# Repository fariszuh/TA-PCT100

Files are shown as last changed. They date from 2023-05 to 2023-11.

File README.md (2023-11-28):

# Tugas  Akhir PCT-100
Repository ini berisi file tugas akhir Implementasi PCT-100.
File yang tersedia berisi file program TA yang dibuat Penulis Muhammad Faris Zuhairi (2019 / Wisudawan 128 ITS), 
dengan judul berikut:

PERANCANGAN KONTROLER TERTANAM MENGGUNAKAN DIRECT NEURAL NETWORK UNTUK PENGATURAN LEVEL TANGKI PCT-100

Link Tugas Akhir: https://repository.its.ac.id/98936/ 
atau pada direktori "**Faris's Undergraduate Thesis (Buku TA)/07111940000164-Undergraduate_Thesis.pdf**"

Berikut foto prototype yang dibuat dan dihibahkan ke Lab. Kontrol dan Otomasi Dept. Teknik Elektro ITS

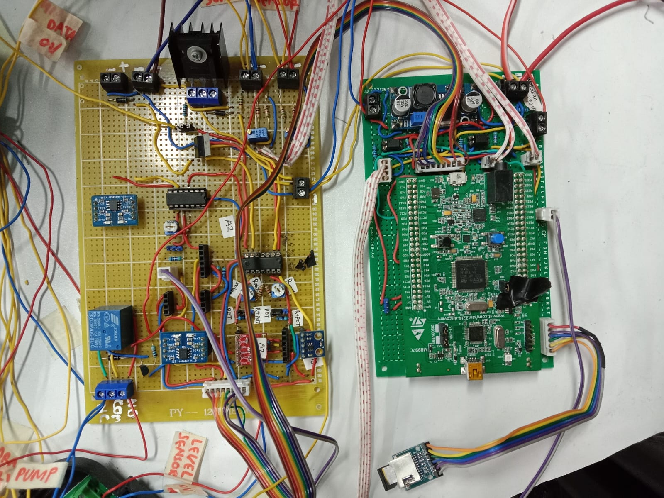
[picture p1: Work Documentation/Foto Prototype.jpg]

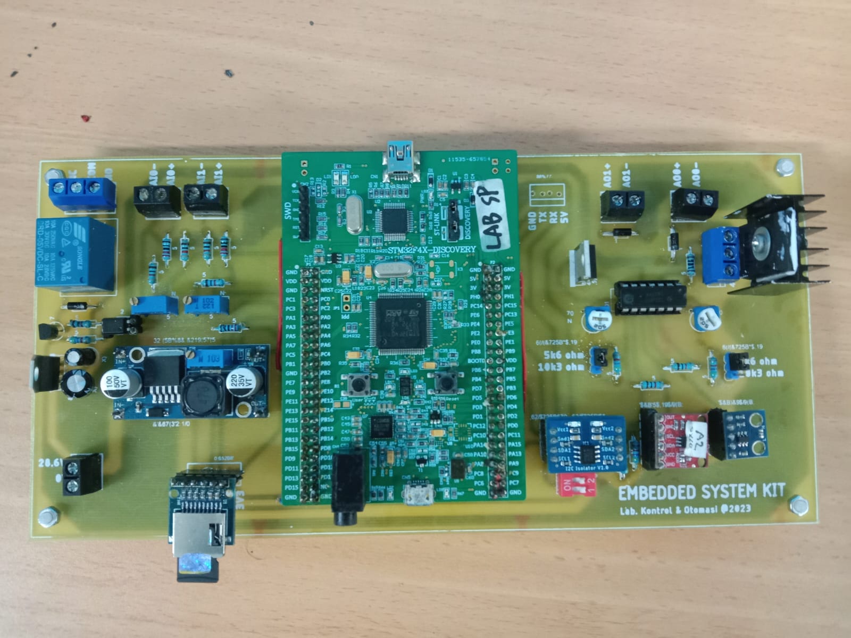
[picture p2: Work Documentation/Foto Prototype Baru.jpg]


## 1. Tahap Permodelan
Tahap ini model plant diambil menggunakan identifikasi plant dan penurunan rumus. 
Permodelan dimulai dengan mengambil data menggunakan STM32 dengan hasil datasets terdapat pada folder berikut:
+ **/Datasets for Modelling & Test Result/**
  - **/Karakteristik Drain Valve/** :
  Data yang digunakan untuk memodelkan drain valve.

    Divariasikan: tegangan drain (Vdrain) dan tegangan flow control valve (Vfc).
    Dijaga konstan: tegangan pompa (Vpompa) 10V.

  - **/Karakteristik Flow Control Valve/** :
  Data yang digunakan untuk memodelkan flow control valve.

    Divariasikan: tegangan pompa (Vpompa) dan tegangan flow control valve (Vfc).
    Dijaga konstan: tegangan drain (Vdrain) tertutup (0 VDC).

  - **/Karakteristik Pompa/** :
  Data yang digunakan untuk memodelkan pompa inlet.

    Divariasikan: tegangan pompa (Vpompa).
    Dijaga konstan: tegangan drain (Vdrain) tertutup (0 VDC) dan dan tegangan flow control valve (22 VDC).

  - **/Karakteristik AI USB4716/** :
    Hasil pengujian DAC Amplifier AO STM32 dengan AI USB4716.
    Pengambilan data ini tanpa menghubungkan prototype ke plant (actuator dan sensor).
    Kode pengujian ini ada di folder **/Pengujian (Testing)/**.
  
    Divariasikan: tegangan AO STM32.

  - **/Karakteristik AO USB4716/** :
    Hasil pengujian ADC AI STM32 dengan AO USB4716.
    Pengambilan data ini tanpa menghubungkan prototype ke plant (actuator dan sensor).
    Kode pengujian ini ada di folder **/Pengujian (Testing)/**.

    Divariasikan: tegangan AO USB4716.

  - **/Pengujian NN/Implementasi/** :
    Hasil pengujian algoritma NN yang ditanam pada STM32.
    Pengambilan data ini dengan menghubungkan prototype ke plant (actuator dan sensor).
  
    Divariasikan: learning rate konstan dan nilai alpha (adaptasi learning rate) --> sudah dipisahkan dalam 2 folder yang berbeda.

  - **/Rafif Firdiansyah's Level Sensor Data/** :
    Excel workbook pembacaan tegangan level sensor dan simpangannya dengan level aktual (cm).

  - **/With Both Drain Valve/** :
    Data yang digunakan untuk memodelkan kedua valve pada kondisi berikut:
    Terbuka: manual dan motor drain valve.
    Tertutup: tidak ada.

      Divariasi: tegangan drain (Vdrain).
    
      Dijaga konstan: tegangan pompa (10 Vpompa) dan tegangan flow control valve (15 Vfc).
  
  - **/with Manual Valve/** :
    Data yang digunakan untuk memodelkan manual valve pada kondisi berikut:
    Terbuka: manual drain valve.
    Tertutup: motor drain valve --> tegangan drain (0 Vdrain) .

      Divariasi: tegangan pompa (Vpompa), dan tegangan flow control valve (Vfc).
    
      Dijaga konstan: full open manual valve.

  - **/with Proportional Drain Valve/** :
    Data yang digunakan untuk memodelkan motor valve pada kondisi berikut:
    Terbuka: motor drain valve.
    Tertutup: manual drain valve.

      Divariasi: tegangan flow control valve (15 Vfc).
    
      Dijaga konstan: tegangan drain (Vdrain) dan tegangan pompa (Vpompa).

Sedangkan, folder berikut berisi file program DAQ untuk pengambilan data plant.

+ **/MATLAB USB-4716/** : pengambilan data melalui DAQ Advantech USB-4716
  - **/Code TA Dedy Motor Induksi & Altivar 610/** : 
  Kode dan Tugas Akhir Dedy / Bambang Permadi Widyasmara tentang Kontrol PID-GA Motor Induksi.
    - Call.m : file utama yang hanya di run untuk mulai mengambil dan mengirim data.
    - ReadWrite.m : file library yang dibuatkan Faris (tidak perlu diubah-ubah).
    
  - **/Code USB4716 TA Faris (Worked)/** :
  File yang sudah diuji dan berhasil membaca AI dan mengirim AO.
    - **/Hasil Pengujian ADC-DAC STM32 dengan USB4716/** :
    Berisi file .mat workspace MATLAB pembacaan pengujian sinyal ramp AI dan AO dari Kit STM32 Implementasi.
    - CascadeController.m : mencoba menyusun kontroler cascade berdasarkan AI-AO
    - InstantAI.m : library default MATLAB untuk analog input DAQ
    - NN.m : mencoba menyusun kontroler Direct NN
    - Static_AO.m : library default MATLAB untuk analog output DAQ
    - Static_AO_custom.m : perubahan Static_AO.m agar bisa mengirim sinyal berubah2 (tidak terbatas default sawtooth, sine, square, dll)
    - Static_AO_simple.m : simplifikasi dari Static_AO_custom.m
  - **/Library Example Bawaan Navigator App/** :
  Library MATLAB yang didapatkan dari tutorial aplikasi Navigator.exe.
  - **/Library python-advantech-DAQNavi-bdaqctrl/** : 
  Library python untuk USB-4716, masih perlu compiler dari C ke python

+ /regresi : regresi respon level dan flow untuk mendapat gain scaling transmitter
  - regresi_FT.m : mencari gain flow meter untuk mengubah tegangan volt ke debit liter/menit (lt/min)
  - regresi_LT.m : mencari gain level sensor untuk mengubah tegangan volt ke level (mm)
+ /write_csv : testing program python data logger
  - save_data_fopen.py : test buka data csv menggunakan fungsi fopen()
  - save_data_withopen.py : test buka data csv menggunakan fungsi withopen()

## 2. Tahap Simulasi
Model yang telah diperoleh pada tahap sebelumnya digunakan untuk desain kontroler. 

+ **/Modelling & PCT-100 Simulation Testing/** :
  - **/MAT simulasi/** : 
  Berisi file .mat workspace MATLAB. Setpoint/SP divariasikan 100mm dan dynamic naik turun.
  MOV divariasi bukaan mulai 0%, 50% (aka 0.5), 100% (aka 1), dan dynamic (uniform random).
  Untuk Learning Rate (lr) konstan, alpha=0 dan lrinit divariasi mulai dari 1e-5 hingga 5.
  Namun, untuk Adaptasi Learning Rate melalui parameter alpha, divariasikan alpha mulai 1e-4 hingga 0.1, dimana alpha identik dengan kecepatan perubahan learning rate (lr).
  
  - **/Proteus DAC PWM/** :
  Berisi simulasi proteus untuk rangkaian PWM generator, amplifier teganan AO, dan filter sebelum diimplementasikan bersama STM32.
  
  - **/Tank Level Modelling/** :
  Simulasi kontroler berdasarkan model. Namun file terbarunya berada diluar folder ini (upper directory sekali).
  - closedLoop.slx : Simulink closed loop system
  - loadDatasets.m : file function matlab untuk membuka datasets untuk permodelan/menampilkan grafik respon
  - modellingDatasets.m : pengolahan raw data plant untuk mendapatkan gain scaling model
  - openLoop.slx : Simulasi open loop system

+ **/Pengujian (Testing)/** : Berisi kode untuk pengujian performa kontroller.
  - pengujian_ADC_AI_STM.m : pengujian ADC AI STM32 dengan menginjeksi tegangan AO sinyal ramp naik turun pada USB4716.
  - pengujian_ADC_A0_STM.m : pengujian DAC A0 STM32 dengan DAC STM32 menginjeksi tegangan sinyal ramp naik turun ke USB4716.
  - pengujian_lr.m : berisi kode untuk plot hasil model NN satu satu dari datasets.

## 3. Tahap Implementasi

+ **/Datasheet and Manual Embedded System Kit/** :
  Berisi datasheet dan manual komponen prototype Embedded System Kit.
  - **/ADAM 5000L-TCP/** : 
  Folder berisi Advantech ADAM5000L TCP installer, modbus simulator, dan RD9700 USB-Ethernet Driver
  
  - **/Manual Advantech USB4716/** :
  Folder berisi datasheet Advantech USB4716 dan Tugas Akhir yang menggunakan perangkat DAQ ini.
  Installer DAQ ini dapat didownload terbaru pada laman resmi Advantech, aplikasi utility dan drivernya ialah Navigator.exe.

  - **/Manual PCT100 by Bytronic/** :
  Folder berisi datasheet PCT-100 dan Burkert Proportional Valve 2835D.

+ **/Embedded System Kit PCB & Acrylic Box/** :
Berisi file PCB dan 3D Akrilik.
  - **/3D Akrilik/** :
  Berisi file cetak akrilik dan gcode 3D print casing USB-TTL Converter. 
  - **/Schematic PCB/** :
  Berisi file PCB Eagle.

+ **/Faris's Undergraduate Thesis (Buku TA)/** :
Berisi dokumen Seminar Tugas Akhir (STA Himatektro ITS) dan Tugas Akhir Faris.

+ **/Konten Sidang (Thesis Defense) dan Proposal/** :
Berisi file proposal (dokumen dan PPT sidang sempro) dan PPT sidang TA.

+ **/Manual Book Embedded System Kit/** :
Berisi manual book dari prototype Embedded System Kit yang sudah dibuat.
Harap pengguna prototype dan asisten Lab. Kontrol dan Otomasi ITS mempelajari ini.

+ **/PCT100 with ADAM 5000L MQTT/** :
  Implementasi PCT100 untuk TA Khoiruz (PID-PSO) dan TA Rafif (fuzzy MQTT) menggunakan ADAM5000L/TCP.

  - **/Modelling & Testing/** : Pengujian kontroler fuzzy dan PID dituning PSO
    - **/Datasets/** : Hasil pengambilan data openloop untuk TA Khoiruz dan Rafif
    - **/multiple subscribe fuzzy/** : testing program MQTT subscribe untuk kontroler fuzzy
        * Close Loop Fuzzy Multiple Subscribe.py : subscribe untuk closed loop system
        * MQTTtestMultipleSubscribe.py : test data masuk MQTT
    - **/scaling_regresi_flow_meter/** : 
    mencari gain scaling flow, raw data dari software PCT100 (bukan DAQ) oleh Khoiruz untuk permodelan plant. 
    - closedLoop_fuzzy.py : kontroler closed loop fuzzy
    - closedLoop_fuzzy_azzam.py : kontroler close loop fuzzy dengan rule base TA Hamzah Nur Azzam Motor Induksi
    - closedLoop_level.py : kontroler PID close loop level khoiruz
    - closedLoop_level_buTri.py : kontroler PID khoiruz hasil revisi penguji Bu Trihastuti
    - openLoop_level_flow.py : open loop untuk mendapat respon level dan flow identifikasi
    - readStreamModbus.py : Reverse engineering informasi stream Modbus UDP dari DAQ ADAM4000L/TCP
    - systemIdentification.py : Identifikasi sistem orde 1 + time delay dan orde 2 sesuai jurnal Jacoubek_Pavel
    - testRampMotorDC_SPA.py : pengujian sinyal kontrol ramp motor DC untuk tugas sistem pengaturan adaptif
    - testTs.py : pengujian untuk memperkecil timesampling Ts Modbus UDP DAQ ADAM4000L
    - testUDPmasAdrian.py : ambil data informasi AI UDP
    - testUDPmodbus2.py : ambil data informasi AI UDP dengan algoritma lain
  - **/Python GUI/** : Test coba desain GUI Python Modbus TCP
  - **/Regresi Sensor/** : berisi regresi level transmitter (LT) dan flow meter (FT).
  - **/Serial STM32/Send Command.py** : berisi kode untuk send command SP, Kp, Ki, Kd ke mikrokontroller STM32 sebagai parameter kontroller.
  - **/List Pin IO ADAM.xlsx** : List pin Input Output ADAM5000L dan berisi address register Modbus TCP.

+ **/Rafif's MQTT Mobile App/** : Settingan MQTT Rafif untuk kontroler fuzzy.
  - **/Konfigurasi APP IoT MQTT Panel/** : Konfigurasi IoT MQTT Panel (Aplikasi PlayStore).
  - testMQTT.py : implementasi python dengan app IoT MQTT Panel (playstore)

+ **/Receipt & Buying Report/** : Kumpulan nota dan laporan keuangan pembuatan prototype Embedded System Kit.
  Budget Rp1juta dari Lab. via Pak Eka Iskandar.
  - Rekap Nota Embedded System Kit_Update 19 Nov 2023.xlsx : Laporan keuangan masuk keluar dan total.

+ **/References for Citation/** : Kumpulan buku dan jurnal penelitian.
  - **/Faris's Journal Reference/** : 
  Referensi jurnal faris untuk neural network dan plant mathematical modelling.
  - **/PID ANFIS Hakhi** : 
  Referensi jurnal Hakhi berkaitan dengan ANFIS.
  - **/Previous Thesis/** : 
  Tugas akhir sebelumnya yang membahas coupled tank, PCT single tank, quadruple tank, NN, dan TA lain yang berkaitan.
  - **/System Identification Journal/** :
  Jurnal referensi identifikasi model system.
  - **/Theory Book/** :
  Buku teori yang dapat digunakan untuk dasar teori bab 2.

+ **/STM32/MultichannelADC/** : Pengujian kontroler dengan program yang sudah tertanam

## Documentation
+ **/Work Documentation/** : 
  berisi dokumentasi pekerjaan dengan Sobat PCT 2023.
### Faris's NN Implementation Video (showed during Final Project Presentation/Sidang TA)
1. PCT100 with constant Set Point https://www.youtube.com/watch?v=iwgPA4LB7lY&ab_channel=MuhammadFarisZuhairi
2. PCT100 with Increasing-Decreasing Set Point (step 50mm) https://www.youtube.com/watch?v=AL7DxppEuDM&ab_channel=MuhammadFarisZuhairi

### Team's Documentation
1. [28/03/2023 - Part 1 Paparan Progress Bimbingan TA PCT-100 at 23:24:33] https://youtu.be/hUXw9mhMRqU
2. [28/03/2023 - Part 2 Paparan Progress Bimbingan TA PCT-100 at 23:34:30] https://youtube.com/shorts/yUkm82Lsc_I
3. [28/03/2023 - Part 3 Paparan Progress Bimbingan TA PCT-100 at 23:35:58] https://youtu.be/i6Gw3u0Zylg
4. [28/03/2023 - Part 4 Paparan Progress Bimbingan TA PCT-100 at 23:44:26] https://youtu.be/1I7eSQTP36s
5. [29/03/2023 - Part 5 Paparan Progress Bimbingan TA PCT-100 at 23:04:08] https://youtu.be/HnbYzEy3LrQ

### Disclaimer
Apabila terdapat kebingungan pada program/struktur repository, silahkan menghubungi author IDLINE: fariszuh

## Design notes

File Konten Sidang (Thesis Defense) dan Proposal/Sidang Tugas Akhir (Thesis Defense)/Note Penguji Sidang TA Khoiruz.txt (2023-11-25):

1. TF harus pake statespace model
2. cascade setidaknya variabel yg dikontrol flow dan level (MIMO) bukan SISO.
3. Tuning PID harus dibandingkan dgn conventional ziegler nichols, conventional narik garris. 
Kp ziegler didekatin dgn Kp PSO
4. Implementasi: aktuatornya 1, yaitu pompa. pompa hanya kontrol level. 
Mintanya p ari kontrol flow, pasti harus ada aktuator lain, agar tidak SISO, seperti Valve.
5. P&ID salah gambar -bu tri, gaadda electric signal ke pump.

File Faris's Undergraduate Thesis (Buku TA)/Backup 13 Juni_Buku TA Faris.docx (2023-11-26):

TUGAS AKHIR – EE184801

PERANCANGAN KONTROLLER TERTANAM MENGGUNAKAN DIRECT SELF TUNING NEURAL NETWORK UNTUK PENGATURAN LEVEL TANGKI PCT-100

MUHAMMAD FARIS ZUHAIRI

NRP 07111940000164

Dosen Pembimbing

Eka Iskandar, S.T., M.T.

NIP 198005282008121001

Dr. Trihastuti Agustinah, S.T., M.T.

NIP 196808121994032001

Program Studi Teknik Sistem Pengaturan

Departemen Teknik Elektro

Fakultas Teknologi Elektro dan Informatika Cerdas

Institut Teknologi Sepuluh Nopember

Surabaya

2023

TUGAS AKHIR – EE184801

PERANCANGAN KONTROLLER TERTANAM MENGGUNAKAN DIRECT SELF TUNING NEURAL NETWORK UNTUK PENGATURAN LEVEL TANGKI PCT-100

MUHAMMAD FARIS ZUHAIRI

NRP 07111940000164

Dosen Pembimbing

Eka Iskandar, S.T., M.T.

NIP 198005282008121001

Dr. Trihastuti Agustinah, S.T., M.T.

NIP 196808121994032001

Program Studi Teknik Sistem Pengaturan

Departemen Teknik Elektro

Fakultas Teknologi Elektro dan Informatika Cerdas

Institut Teknologi Sepuluh Nopember

Surabaya

2023

FINAL PROJECT – EE184801

EMBEDDED CONTROLLER DESIGN USING DIRECT SELF TUNING NEURAL NETWORK FOR LEVEL CONTROL IN PCT-100 TANK

MUHAMMAD FARIS ZUHAIRI

NRP 07111940000164

Advisor

Eka Iskandar, S.T., M.T.

NIP 198005282008121001

Dr. Trihastuti Agustinah, S.T., M.T.

NIP 196808121994032001

Study Program Control System Engineering

Department of Electrical Engineering

Faculty of Intelligent Electrical and Informatics Technology

Institut Teknologi Sepuluh Nopember

Surabaya

2023

# LEMBAR PENGESAHAN

PERANCANGAN KONTROLLER TERTANAM MENGGUNAKAN DIRECT SELF TUNING NEURAL NETWORK UNTUK PENGATURAN LEVEL TANGKI PCT-100

TUGAS AKHIR

Diajukan untuk memenuhi salah satu syarat

memperoleh gelar Sarjana Teknik pada

Program Studi S-1 Teknik Sistem Pengaturan

Departemen Teknik Elektro

Fakultas Teknologi Elektro dan Informatika Cerdas

Institut Teknologi Sepuluh Nopember

Oleh : MUHAMMAD FARIS ZUHAIRI

NRP. 07111940000164

Disetujui oleh Tim Penguji Tugas Akhir :

1. | Eka Iskandar, S.T., M.T. | Pembimbing
2. | Dr. Trihastuti Agustinah, S.T., M.T. | Ko-pembimbing
3. | Nama dan gelar penguji | Penguji
4. | Nama dan gelar penguji | Penguji
5. | Nama dan gelar penguji | Penguji

SURABAYA

Juni, 2023

# PERNYATAAN ORISINALITAS

Yang bertanda tangan di bawah ini:

Nama mahasiswa / NRP | : | Muhammad Faris Zuhairi
Program studi | : | Teknik Sistem Pengaturan
Dosen Pembimbing / NIP | : | Eka Iskandar, S.T., M.T. / 198005282008121001 Dr. Trihastuti Agustinah, S.T., M.T. / 196808121994032001

dengan ini menyatakan bahwa Tugas Akhir dengan judul “Perancangan Kontroller Tertanam Menggunakan Direct Self Tuning Neural Network untuk Pengaturan Level Tangki PCT-100” adalah hasil karya sendiri, bersifat orisinal, dan ditulis dengan mengikuti kaidah penulisan ilmiah.

Bilamana di kemudian hari ditemukan ketidaksesuaian dengan pernyataan ini, maka saya bersedia menerima sanksi sesuai dengan ketentuan yang berlaku di Institut Teknologi Sepuluh Nopember.

Surabaya, 10 Juni 2023

Mengetahui,
Dosen Pembimbing 1 | Dosen Pembimbing 2
Eka Iskandar, S.T., M.T. | Dr. Trihastuti Agustinah, S.T., M.T.
NIP. 198005282008121001 | NRP. 196808121994032001

Mahasiswa

Muhammad Faris Zuhairi

NRP. 07111940000164

# ABSTRAK

PERANCANGAN KONTROLLER TERTANAM MENGGUNAKAN DIRECT SELF TUNING NEURAL NETWORK UNTUK PENGATURAN LEVEL TANGKI PCT-100

Nama Mahasiswa / NRP | : | Muhammad Faris Zuhairi/07111940000164
Departemen | : | Teknik Elektro FTEIC - ITS
Dosen Pembimbing | : | Eka Iskandar, S.T., M.T. Dr. Trihastuti Agustinah, S.T., M.T.

Abstrak

Kata kunci: PCT-100, Neural Network, Self Tuning, Sistem Tertanam

# ABSTRACT

PERANCANGAN KONTROLLER TERTANAM MENGGUNAKAN DIRECT SELF TUNING NEURAL NETWORK UNTUK PENGATURAN LEVEL TANGKI PCT-100

Student Name / NRP | : | Muhammad Faris Zuhairi/07111940000164
Department | : | Teknik Elektro FTEIC - ITS
Advisor | : | Eka Iskandar, S.T., M.T. Dr. Trihastuti Agustinah, S.T., M.T.

Abstract

Keywords: PCT-100, Neural Network, Self Tuning, Embedded System.

# DAFTAR ISI

# DAFTAR GAMBAR

# DAFTAR TABEL

# DAFTAR SIMBOL

# BAB 1 PENDAHULUAN

## 1.1 Latar Belakang

Saat ini industri proses banyak menerapkan sistem otomasi pengaturan level fluida. Fluida dipompa dan ditampung dalam tangki khusus yang memerlukan pengendalian agar memenuhi batas level yang diperbolehkan. Umumnya level air dianalisis dengan mengestimasi model linear yang merepresentasikan sifat dinamis dari level terhadap titik setimbangnya. Apabila ketinggian cairan tidak dikendalikan maka rantai proses produksi akan terganggu. Jika ketinggian cairan melebihi ketinggian yang diinginkan maka akan terjadi overflow atau cairan akan meluap sehingga mengganggu atau dapat merusak alat-alat lain. Sebaliknya jika ketinggian cairan kurang dari ketinggian yang diinginkan maka proses tidak akan bekerja. Oleh karena itu ketinggian suatu cairan harus dikendalikan dalam suatu industri.

Umumnya dalam industri, fluida dialirkan menggunakan pompa, laju massa diatur dengan control valve, dan ketinggian fluida dalam tangki dibaca oleh level transmitter. Namun, pengaturan level tangki memiliki karakteristik time-varying dan non linier. Kontroller PID membutuhkan parameter berbeda-beda (tuning ulang) untuk menyesuaikan respon yang cepat. PCT-100 merupakan miniatur sistem proses industri yang terdapat fasilitas untuk melakukan pengaturan terhadap empat buah variable kontrol, yaitu flow, level, suhu, dan tekanan. Level pada plant PCT-100 yang dikendalikan oleh flow control valve seringkali mengalami perubahan parameter dalam kondisi-kondisi tertentu, seperti adanya beban drain air keluar. Untuk mengatasi perubahan ini, diperlukan metode yang dapat belajar (learning) terhadap perubahan. Selain itu, flow control valve memiliki karakteristik khusus yakni daya suplai yang dibutuhkan besar yang membutuhkan penguatan dan hardware terpisah untuk menjalankannya.

Salah satu metode learning yang menggunakan algoritma cerdas ialah neural network. Algoritma ini dapat mempelajari perubahan beban pada plant dan akan otomatis melakukan updating bobot selama plant beroperasi sehingga mudah memenuhi spesifikasi kontrol yang diinginkan. Dengan struktur direct, kontroller dapat langsung memberikan sinyal kontrol sesuai berdasar error setpoint variable sistem yang dikendalikan. Namun, pemilihan learning rate pada propagasi balik masih perlu dilakukan manual berdasar hasil eksperimen, sehingga jika kurang tepat memungkinkan terjadinya overshoot level. Skema self tuning dapat ditambahkan agar learning rate dapat beradaptasi sesuai error level. Pada tugas akhir ini akan dirancang controller tertanam menggunakan self tuning direct neural network plant PCT-100 yang meminimalkan error steady state dan mengurangi overshoot.

## 1.2 Rumusan Masalah

Kontroller PID pada dasarnya bersifat tetap selama parameter P, I, dan D tidak diubah. Ketika terjadi perubahan parameter plant yang diakibatkan oleh pembebanan, sinyal kontrol yang diberikan tidak sesuai dengan kondisi plant saat ini sehingga muncul pelonjakan atau penurunan nilai. Pada level tangki PCT-100, kondisi ini dapat diakibatkan oleh perubahan beban drain valve selama sistem berjalan sehingga parameter kontroller perlu dituning ulang terus menerus. Penggunaan neural network sebagai direct controller memiliki keunggulan dapat beradaptasi pada model nonlinear, namun pemilihan learning rate masih dilakukan manual dengan eksperimen. Selain itu, flow control valve sebagai actuator memiliki daya suplai tinggi (0-24V, 1A) dan tidak bisa dijalankan oleh modul data actuisition yang tersedia. Berdasarkan masalah nonlinearity, learning rate, dan aktuator tersebut, dibutuhkan kontroller tertanam dan menambahkan self tuning learning rate yang dapat melakukan pemilihan learning rate yang sesuai secara langsung (online tuning) agar steady state error dapat minimum.

## 1.3 Batasan Masalah

Ruang lingkup penelitian ini membahas mengenai pengaturan level pada tangki. Pengendalian level dilakukan oleh flow control valve dengan tegangan pompa konstan. Batasan lain yaitu mengabaikan efek temperature dan pressure dalam tangki proses.

## 1.4 Tujuan

Tujuan yang diharapkan dari penelitian ini ialah rancangan kontroller tertanam neural network mampu mengatasi masalah nonlinearity, adaptasi learning rate, dan penguatan sinyal actuator untuk mendapat error steady state dan overshoot yang minimum.

## 1.5 Manfaat

Manfaat yang dapat diperoleh melalui tugas akhir ini diantaranya memberikan pengembangan metode kontrol dari pengaturan level tangki nonlinear dan memberikan skema penguatan actuator yang tidak dapat dijalankan oleh data actuisition module biasa.

# BAB 1 TINJAUAN PUSTAKA

## 1.1 Hasil Penelitian Terdahulu

Penelitian terdahulu digunakan untuk mengetahui metode dan hasil penelitian yang sudah dilakukan. Penelitian terdahulu diperlukan sebagai landasan dan acuan peneliti terhadap perbandingan dan hubungan antar variable yang diuji.

Penelitian plant PCT-100 oleh Rachmad Dwi Raharjo (2014) dilakukan dengan metode PID gain scheduling terhadap level proses. Identifikasi sistem dilakukan dengan metode Harriot dan divalidasi menggunakan ISE/Integral Square Error. Hasil yang diperoleh yakni kontroller PID gain scheduling dapat mengendalikan respon dinamis dalam simulasi dengan rata-rata error waktu tunak 0.06% dan 0.12% pada implementasi. Namun, nilai gain PID masih dipengaruhi variable tertentu yang berubah kontinu atau dengan kata lain gain scheduling hanya cocok untuk variasi yang terprediksi.

Penelitian level proses kemudian disempurnakan oleh penelitian M. Zakki Ghufron (2016) yang menggunakan self-tuning PID dengan pendekatan adaptif. Kontroller adaptif dapat memperbaiki kelemahan metode gain scheduling, dimana dapat bekerja pada variasi tak terprediksi. Nilai gamma memengaruhi kecepatan adaptasi kontroller self tuning PID. Kriteria square time-square error/STSE unggul karena memberikan error terkecil 3.64% saat simulasi dan 0.093% bila diberikan pembebanan. Namun, implementasinya masih memerlukan waktu learning yang lama dan memerlukan otomatisasi penentuan nilai gamma.

Berdasarkan penelitian PCT-100 sebelumnya, diharapkan desain kontroller PID yang detuning menggunakan metode neural network dapat memberikan waktu yang cepat dalam proses learning.

Gambar x. Training neuron

Penelitian direct neural network oleh memberikan hasil yang efektif untuk mengatur posisi sudut alloy manipulator dengan maksimum error 0.83°. Bobot (weight) neural network diperbarui berdasarkan feedback sensor posisi. Karakteristik nonlinear hysteresis 1 DOF manipulator dapat dihilangkan dan posisi sudut mengikuti set point yang berbentuk gelombang sinus.

## 1.2 Dasar Teori

### 1.2.1 PCT-100

PCT-100 merupakan mini-plant industry yang didesain untuk pembajaran berbagai aplikasi industry. Produk bytronic ini menggabungkan beberapa proses menjadi unit tunggal sehingga memberikan fleksibilitas dan kemudahan operasi sistem proses. Air sebagai fluida dalam process rig dapat dikendalikan melalui control box dan PC software. Besaran ini meliputi temperature, level, pressure, dan flow. Eksperimen dengan metode kontrol bervariasi dapat dilakukan dengan mudah untuk mendapatkan respon variable process yang diinginkan.

#### 1.2.1.1 Process Rig

Process rig merupakan plant utama tempat proses berlangsung. Air distilasi yang ditampung dalam sump tank dipompa ke seluruh sistem pada flow sekitar 3.2 liter/menit. Air dapat dialirkan langsung menuju process tank atau dibelokkan menuju cooler. Flow meter mengukur flow rate air yang masuk process tank dan level sensor akan mengukur ketinggian permukaannya. Di dalam process tank, pressure dan temperature air dapat diukur. Air dalam tangki ini dapat dikeluarkan melalui manual atau proportional drain valve untuk mengakhiri satu siklus proses. Process rig juga dilengkapi dengan digital display untuk menunjukkan temperature, flow, pressure, dan level saat ini, serta indicator on/off dari cooler, heater, diverter, dan drain valve. PCT-100 tersusun atas beberapa elemen berikut.

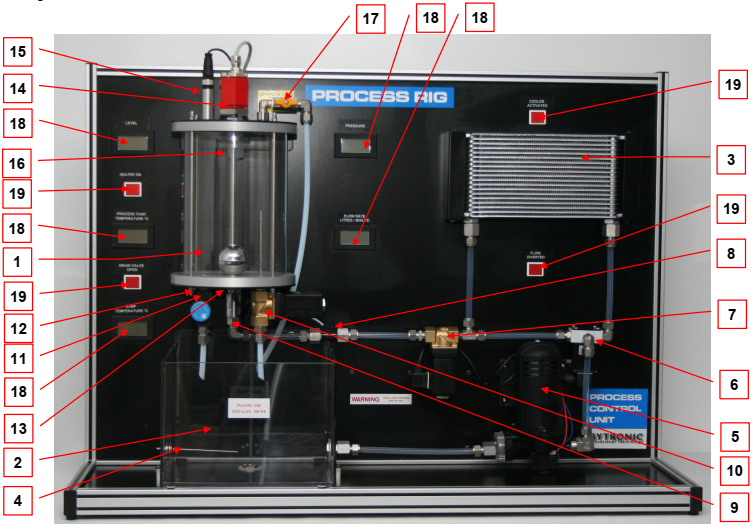
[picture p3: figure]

Gambar 2.1 Process Rig PCT-100

Tabel 2.1 Komponen process rig

No. | Perangkat
1 | Process tank
2 | Sump tank
3 | Cooler Unit
4 | Sump tank Temperature sensor (PRT)
5 | Variable speed pump with filter and pressure switch
6 | 3/2 Diverter valve
7 | 2/2 Proportional control valve
8 | Flow rate sensor
9 | One way check valve
10 | 2/2 Proportional drain valve
11 | Needle valve
12 | Pressure relief valve
13 | Heater
14 | Level sensor
15 | Pressure transducer
16 | Float switch
17 | Overflow/Vent valve
18 | Digital LCD displays
19 | Indicator lights

#### 1.2.1.2 Control Module

Control module merupakan perangkat yang berfungsi memberikan mengolah sinyal kontrol untuk diteruskan pada process rig. Control module mengolah sinyal input standar 0-10VDC menjadi tegangan suplai tiap actuator, serta mengkondisikan sinyal sensor menjadi sinyal standar 0-10VDC. Bagian depan perangkat ini menampilkan P&ID process rig yang dilengkapi dengan indicator on/off, fault switch, dan test point.

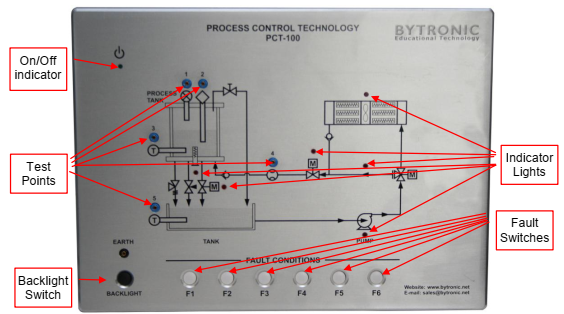
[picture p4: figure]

Gambar 2.2 Control Module

#### 1.2.1.3 Embedded Data Actuisition

Akuisisi data dilakukan untuk mengolah sinyal sensor sekaligus mengirimkan sinyal actuator dari dan ke control module. STM32F407VG digunakan sebagai mikrokontroller untuk memproses sinyal input 0-5V dan output ke DAC. MCP4725 DAC

### 1.2.2 Permodelan Plant

Sebelum melakukan desain kontroller, model plant perlu diketahui agar parameter kontroller sesuai dengan batas spesifikasi plant yang diimplementasi. Berikut merupakan arsitektur hardware PCT-100 beserta plant proses yang digunakan.

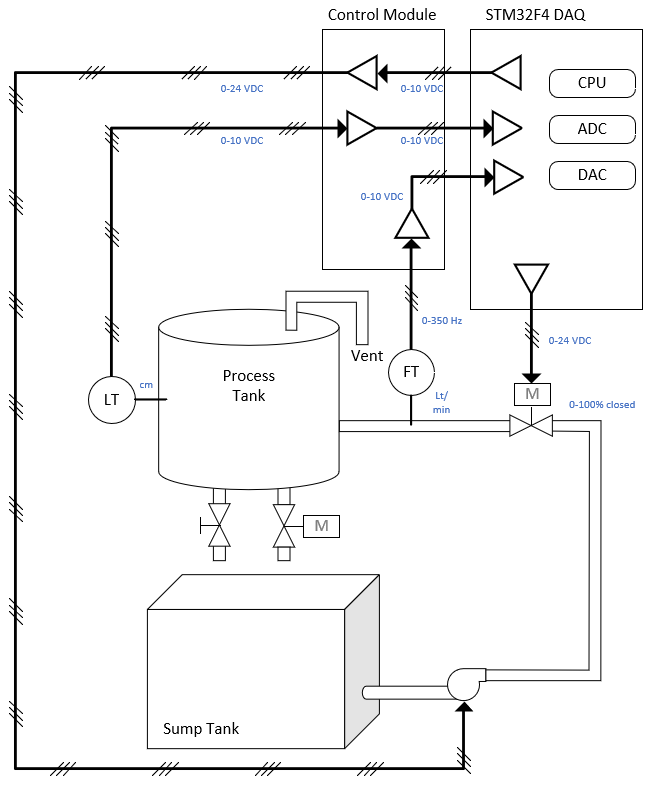
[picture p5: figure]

Gambar 2.2 Arsitektur Hardware PCT-100

#### 1.2.2.1 Permodelan Level Sensor

Level transmitter merupakan instrument pengukur ketinggian permukaan air menjadi tegangan searah dengan menggunakan level sensor. Pada level sensor terjadi konversi besaran ketinggian air menjadi tegangan. Faktor pengali ketinggian air ke tegangan dicari mula-mula dengan mengambil 4 sampel tegangan level sensor dari input ketinggian tertentu menggunakan jangka sorong, yakni 80.8mm, 128.4mm, 171.5mm, dan 208.15mm. Ketinggian air ini diambil pada jangkauan pergerakan floating ball untuk menghasilkan output tegangan sensor, yakni antara 30mm (bola mulai bergerak) hingga 210mm (bola berhenti bergerak). Secara konstruksi level sensor memiliki batas bawah awal bergerak dan batas akhir bergerak yang tergambar pada gambar dibawah.

Gambar 4.1 Penempatan floating ball pada tangki proses

Keluaran tegangan level sensor ( V_(LT) ) terhadap variasi ketinggian air (h), kemudian dilakukan regresi linier untuk mendapat persamaan garis lurus.

V_(LT) (h)=G_(LT) h+c_(LT)

G_(LT) =(V_(LT 4) -V_(LT 1))/(h_4 -h_1)

c_(LT) =V_(LT 4) -G_(LT) h_4

#### 1.2.2.2 Permodelan Flow Meter

Flow meter mengukur laju air masuk ke tangki proses. Laju ini dikenal dengan debit, yaitu laju volume per satuan waktu.

Q_(in) =(∆V)/(∆t)=A_(tabung) (∆h)/(∆t)

Input berupa laju air dikonversi oleh impeller turbin menjadi sinyal pulsa kemudian diproses signal conditioning. Output sensor flow ini ialah tegangan 0-10V. m_(FT) ialah factor konversi mikrokontroller dari input tegangan flow meter menjadi debit masukan.

Q_(in) =m_(FT) V_(FT)

Namun, model plant flow meter didapatkan dari input fisik laju ketinggian air (∆h)/(∆t) dan tegangan flow meter V_(FT) sebagai output sensor.

m_(FT) V_(FT) =A_(tabung) (∆h)/(∆t)

V_(FT) (h)=(A_(tabung))/(m_(FT))(∆h)/(∆t)

Misalkan gain model flowmeter adalah G_(FT) =(A_(tabung))/(m_(FT)) , model instrument flowmeter menjadi

V_(FT) (h)=G_(FT) (∆h)/(∆t)

#### 1.2.2.3 Permodelan Flow Control Valve

Permodelan flow valve ditujukan untuk mengetahui karakteristik bukan valve terhadap flow output pompa. Model flow control valve merupakan transfer function dari tegangan valve sebagai input dan flow rate air sebagai outputya. Model ini diperoleh dengan melakukan variasi tegangan valve, yakni 13V,15V,18V, dan 21V yang diperoleh terhadap tegangan step pompa 10V. permodelan flow control valve menggunakan metode vitechkova yang mengambil respon step saat 33% dan 70% nilai steady state. Sistem didekati oleh model orde 1 dengan menyertakan time delay model.

G_(V1) (s)=K/(τ_(V1) s+1)e^(-T_(dV1) s)

Dimana t_33 dan t_70 masing-masing ialah waktu 33% dan 70% dari nilai steady steate.

T_(dV1) =1.498t_33 -0.498t_70

τ_(V2) =0.794(t_70 -t_33 )

#### 1.2.2.4 Permodelan Drain Valve

Gambar 2.3 Bagan sistem tangki tunggal

Drain valve mengikuti prinsip konservasi energi, dimana persamaan Bernoulli menyatakan hubungan tekanan, laju fluida, dan ketinggian cairan dalam suatu tangki. Titik pada permukaan air dan dasar tangki bagian luar memiliki tekanan yang sama ( P_(permukaan) =P_(out) =1 atm ), namun memiliki kecepatan turun dan tinggi fluida yang berbeda.

P_(permukaan) +1/2ρv_(permukaan)^2 +ρgh_(permukaan) =P_(out) +1/2ρv_(out)^2 +ρgh_(out) =constant

1/2ρ(v_(out)^2 -v_(permukaan)^2 )=ρg(h_(permukaan) -h_(out) )

Kecepatan penurunan permukaan air dianggap sangat kecil sehingga diabaikan v_(permukaan) =0 dan lubang drain berada di dasar tangki h_(out) =0 .

1/2ρv_(out)^2 =ρgh

v_(out) =√(2gh)

Flow dapat dirumuskan sebagai laju air per satuan waktu, dengan A_O ialah luasan aperture drain valve.

Q_(out) =A_O v_(out) =A_O √(2gh)

#### 1.2.2.5 Permodelan Tangki

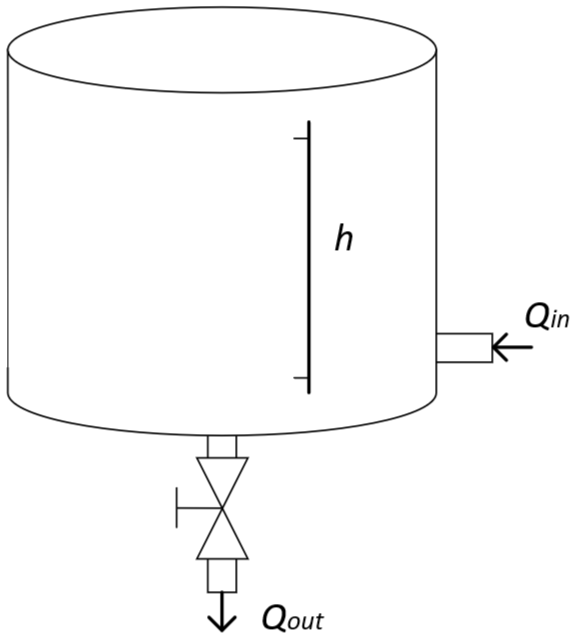
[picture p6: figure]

Gambar 2.5 Sistem tangki tunggal

Model dari tangki tunggal tampak pada gambar di atas. Untuk tangki ini, persamaan differensial level dapat dirumuskan sebagai berikut.

A_(tabung) h(t)=Q_(in) (t)-Q_(out) (t)

Dimana A_(tabung) : luas alas tabung, Q_(in) : flow air masuk tangki, Q_(out) : flow keluar tangki

A_(tabung) h(t)=Q_(in) (t)-A_O √(2gh)

Model ini menunjukkan dengan jelas persamaan nonlinear karena flow yang keluar tangki bergantung akar dari level tangki saat ini. Namun, persamaan tersebut dapat dilinearisasi dengan menganggap √h=h/√h seperti Berikut.

h(t)=bQ_(in) (t)-a(t)h(t)

Dimana b=1/(A_(tabung)) dan a(t)=(A_O √(2g))/(A_(tabung) √h)

Ketika h(t)=1 , parameter a(t) bernilai (A_O √(2g))/(A_(tabung) √h) sebagai lokasi pole ketinggian air. Lokasi pole ini terus mendapat scaling sejalan dengan akar dari level h saat ini. Transfer function sistem level orde 1 dapat dirumuskan melalui operator time derivative ‘s’ sebagai Berikut.

s h(t)=bQ_(in) (t)-a(t)h(t)

(s+a(t)) h(t)=bQ_(in) (t)

(h(t))/(Q_(in) (t))=b/(s+a(t))

a(t) dipilih pada posisi h tertentu saat valve drain full open dan memenuhi persamaan Berikut.

Q_(in) -Q_(out) =Ah

Q_(in) (t)-A_O √(2gh(t))=Ah

A_O √(2gh(t))=Q_(in) (t)-Ah

A_O =(Q_(in) (t)-Ah)/(√(2gh(t)))

Dimana h diambil dari gradien kurva level terhadap waktu, Q_(in) (t) dan h(t) masing-masing merupakan flow dan level air pada saat t tertentu.

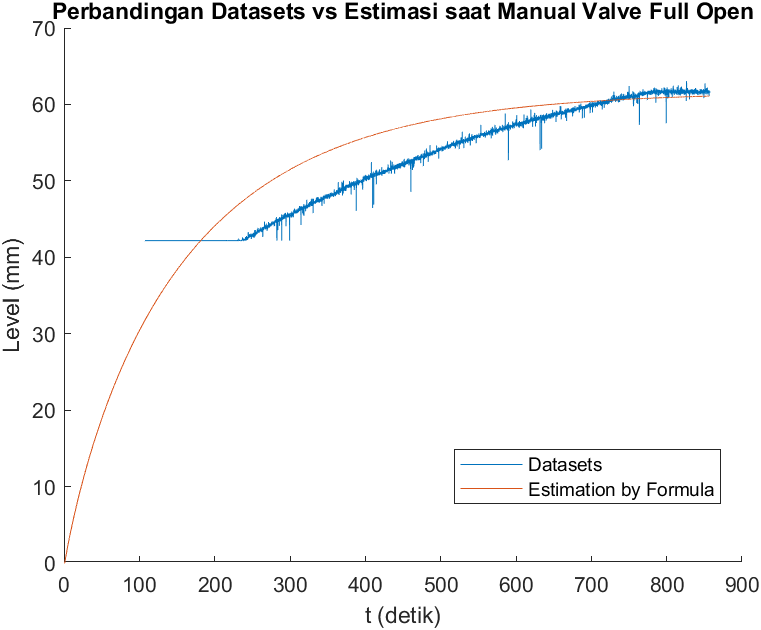
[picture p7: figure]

Gambar 3.2 Perbandingan datasets dengan estimasi model jika hanya manual valve full open

### 1.2.3 Direct Control Neural Network

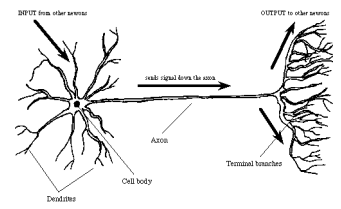
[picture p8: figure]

Gambar xx. Sel syaraf dan bagiannya

Neural Network bekerja menurut prinsip jaringan syaraf manusia. Dari Gambar di atas dapat dilihat, bahwa sebuah neuron mendapatkan input dari dendrit dan memberikan output melalui akson. Informasi masuk kedalam syaraf melalui dendrit. Dendrit ini bertugas mengumpulkan informasi dan meneruskannya ke badan sel. Pada badan sel, informasi yang telah dikumpulkan diolah dengan proses tertentu dan menghasilkan sinyal output. Output dari badan sel diteruskan ke sel syaraf berikutnya melalui akson. Akson ini akan terhubung dengan dendrit sel syaraf berikutya. Sambungan akson sel syaraf satu dengan dendrit sel syaraf lainnya disebut sinapsis. Kekuatan sambungan pada sinapsis menentukan seberapa besar informasi yang diteruskan oleh sel syaraf sebelumnya dapat diterima oleh sel syaraf berikutnya, yang kemudian disebut dengan bobot.

Tiruan neuron dalam struktur Neural Network adalah sebagai elemen proses yang dapat berfungsi seperti halnya sebuah neuron. Model dari neuron pada Neural Network ini seperti pada Gambar 2.8, dimana pi merupakan input pada neuron dan wi merupakan bobot atau weight. Sinyal input pi ini akan dikalikan dengan nilai wi. Nilai output dari neuron ini dapat dirumuskan seperti pada Persamaan berikut

Gambar xx. Blok diagram self-tuning neural regulator

Direct control neural network mengacu paga

Koefisien bobot w_(ji) dan v_j untuk hidden layer.

Untuk menurunkan algoritma backpropagation, cost function error dapat didefinisikan sebagai Berikut.

E(t)=1/2∑_(k=1)^t [e_y (k)]^2

S_j =∑_(i=1)^3 w_(ji) x_i

h_j =1/(1+e^(-S_j)), j=1,2,3…

r=∑_(j=1)^3 v_j h_j

u(t)=1/(1+e^(-r))

(∂E(t))/(∂v_j)=(∂E(t))/(∂e_y)(∂e_y)/(∂e_u)(∂e_u)/(∂u(t))(∂u(t))/(∂r)(∂r)/(∂v_j)

Dimana

(∂E(t))/(∂e_y)=(∂{1/2∑_(k=1)^t [e_y (t)]^2 })/(∂e_y)=e_y

(∂e_u)/(∂u(t))=(∂(u_d (t)-u(t)))/(∂u(t))=-1

(∂r)/(∂v_j)=(∂{∑_(j=1)^3 v_j h_j })/(∂v_j)=h_j

Turunan u(t) terhadap r(t)

(∂u(t))/(∂r)=(∂(1/(1+e^(-r))))/(∂r)=(e^(-r))/((1+e^(-r) )^2)

(∂u(t))/(∂r)=(e^(-r))/(1+e^(-r))1/(1+e^(-r))=u(t)[1-u(t)]

Dimisalkan δ^1 =e_y u(t) [1-u(t)]

(∂E(t))/(∂w_(ji))=-δ^1 v_j h_j (1-h_j )x_i (∂e_y)/(∂e_u)

Dimisalkan δ_j^2 =δ^1 v_j h_j (1-h_j )

(∂E(t))/(∂w_(ji))=-δ_j^2 x_i (∂e_y)/(∂e_u)

v_j (t+1)=v_j (t)+η sign((∂e_y)/(∂e_u)) δ^1 h_j

w_(ji) (t+1)=w_(ji) (t)+η sign((∂e_y)/(∂e_u)) δ_j^2 x_i

# BAB 2 METODOLOGI

## 2.1 Metode yang digunakan

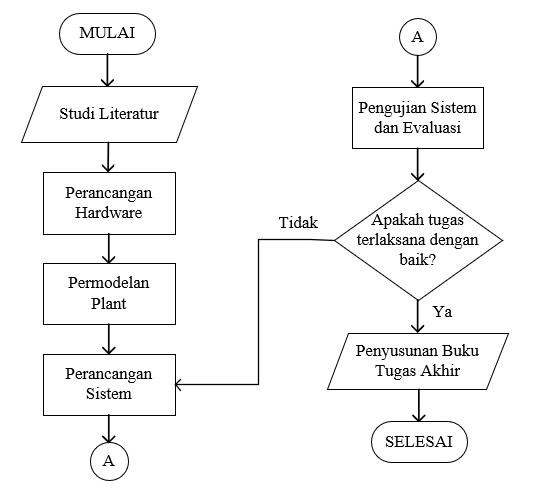
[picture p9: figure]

Gambar 3.3. Flowchart Metodologi Penelitian

Tahapan penelitian yang dilakukan pada tugas akhir ini tersaji pada flow chart gambar xx. Berikut penjelasan dari tahapan yang dilakukan tersebut.

1. Studi literatur

Tahap studi literatur digunakan untuk mengkaji teori-teori yang berhubungan perancangan kontroller sistem level dan desain rangkaian. Selain itu, dikaji pula konsep neural network dan proses learning. Sumber-sumber yang digunakan pada tahap ini berasal dari textbook, manual, datasheet, dan jurnal penelitian sebelumnya.

2. Perancangan hardware

Pada tahap perancangan hardware, hasil kajian tentang rangkaian digunakan sebagai bahan desain hardware. Perancangan ini meliputi desain mikrokontroller dan desain penggerak actuator. Hasil rancangan diuji dengan memberikan sampel sinyal dan mengevaluasi keluarannya apakah masih dalam range simpangan yang diperbolehkan.

3. Permodelan plant dan kontroller

Untuk mengidentifikasi model plant, rancangan hardware dijalankan untuk mendapatkan respon open loop sistem. Permodelan plant meliputi permodelan sensor, actuator, dan tangki proses. Metode identifikasi yang digunakan yaitu penurunan rumus fisis dan vitechkova. Setelah model plant dikatahui, didesain juga sistem closed loop dengan kontroller direct control neural network.

4. Pengujian sistem dan evaluasi

Pengujian sistem dilakukan melalui 2 tahapan, yaitu pengujian dengan simulasi dan pengujian implementasi. Rancangan kontroller disimulasikan pada software Simulink dan respon uji closed loop dievaluasi. Performa sistem berupa Agar algoritma simulasi dapat diimplementasi ke mikrokontroller, program Simulink perlu diubah menjadi Bahasa C. program ini kemudian ditanam pada mikrokontroller untuk pengujian implementasi. Respon implementasi menentukan keberhasilan model dan kontroller yang sudah didesain.

5. Penyusunan buku tugas akhir

Hasil penelitian yang sudah diperoleh kemudian disusun menjadi laporan berupa buku tugas akhir.

## 2.2 Bahan dan peralatan yang digunakan

Alat dan bahan yang digunakan dalam pengerjaan tugas akhir ini diantaranya ialah:

1. Plant PCT-100 sebagai plant utama yang ingin dikontrol
2. Laptop untuk simulasi dan penyusunan buku tugas akhir
3. STM32F407VGT6 Discovery sebagai mikrokontroller tempat program ditanam
4. Modul DAC MCP4725 untuk mengubah sinyal digital menjadi sinyal kontrol analog
5. Rangkaian voltage amplifier (LM324N dan Power MOSFET) sebagai modul penguatan sinyal kontrol ke actuator.

## 2.3 Urutan pelaksanaan penelitian

### 2.3.1 Permodelan Plant

#### 2.3.1.1 Permodelan Level Sensor

Respon tegangan sensor terhadap 4 sampel ketinggian air tampak pada gambar di bawah.

Gambar 4.1 Respon tegangan level sensor terhadap ketinggian air

Perhitungan gradien dan konstanta persamaan garis V_(LT) (h) digunakan 2 sampel level terendah h_0 =80.8mm dan tertinggi h_4 =208.15mm . Nilai tegangan pada kedua titik ini disubstitusi ke persamaan m dan c untuk memperoleh persamaan garis. G_(LT) merupakan gain level sensor dengan input berupa level dan output tegangan sensor.

G_(LT) =(9.4739-2.2046)/(208.15-80.8)=0.0571 Volt/mm

c_(LT) =9.4739-(0.0571*208.15)=-2.4076 Volt

Fungsi tegangan output V_(LT) (Volt) terhadap input ketinggian air level sensor h(mm) diperoleh sebagai fungsi persamaan linier berikut.

V_(LT) (h)=0.0571 h-2.4076

Fungsi level sensor untuk jangkauan dari dasar hingga dinding atas tangki dirumuskan oleh persamaan Berikut.

V_(LT) (h)={, 0 ;h<42.178mm, 0.0571 h-2.4076 ;42.178mm≤h≤217.324mm, 9.997 ;217.324mm≤h

h(V_(LT) )=(V_(LT) +2.4076)/0.0571=17.5189 V_(LT) +42.1780

#### 2.3.1.2 Permodelan Flow Meter

Identifikasi model flow meter diberikan dengan memberi variasi tegangan pompa. Berikut respon flow masuk tangki terhadap tegangan output pembacaan sensor V_(FT) .

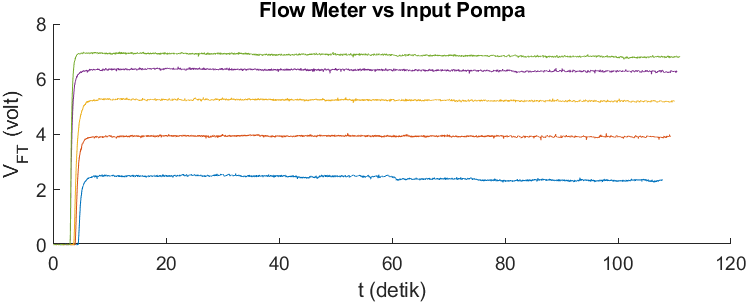
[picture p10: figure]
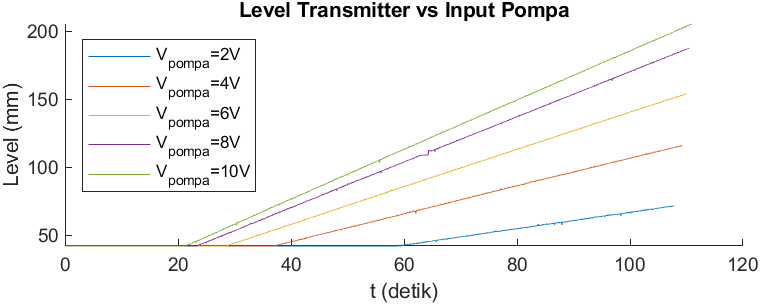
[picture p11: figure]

Gambar xx. Respon tegangan flow dan level terhadap variasi tegangan pompa

Perhitungan gain flow meter diperoleh dari pertambahan ketinggian air dan nilai steady state tegangan flow meter. Persamaan V_(FT) (h) merupakan persamaan garis lurus, sehingga gradien dan konstantanya dapat dicari berdasarkan sampel variasi flow. Variasi flow didapat dengan mengatur tegangan supply pompa, yakni 2V, 4V, 6V, 8V, dan 10V. Masing-masing tegangan ini terbaca flow meter sebesar 2.4011V, 3.9197V, 5.2441V, 6.3062V, dan 6.8518V.

V_(pompa) | V_(FT) steady state | Awal floating ball bergerak | | Setelah 120s runtime
| | t | V_(LT) | t | V_(LT)
2V | 2.4011 | 58837ms | 0 | 107873ms | 1.6992
4V | 3.9197 | 36762ms | 0.0171 | 109283ms | 4.2017
6V | 5.2441 | 28463ms | 0.0146 | 109974ms | 6.3794
8V | 6.3062 | 23408ms | 0.0098 | 110449ms | 8.3081
10V | 6.8518 | 21199ms | 0.0049 | 110928ms | 9.3140

Nilai V_(LT) ini kemudian dikonversi menjadi h dalam satuan mm oleh persamaan sebelumnya, yakni

h(V_(LT) )=17.5189 V_(LT) +42.178

Flow inlet tangki proses akan meningkatkan ketinggian air secara bertahap. Model flow meter didapatkan dalam kondisi drain valve tertutup dan floating ball berada pada jangkauan geraknya. Pada permodelannya, dihitung laju perubahan level naik ( dh/dt ) untuk mendapat tegangan flow meter V_(FT) sebagai output. Substitusi persamaan sebelumnya, V_(FT) (h)=(A_(tabung))/(m_(FT))(∆h)/(∆t) . A_(tabung) dan m_(FT) selalu tetap, namun V_(FT) berubah bergantung laju (∆h)/(∆t) sehingga dapat dirumuskan sebagai persamaan garis lurus V_(FT) (h)=(A_(tabung))/(m_(FT)) ((∆h)/(∆t))+c_(FT) seperti berikut.

gradien=(A_(tabung))/(m_(FT))=(V_(FT V_(pompa) =10V) -V_(FT V_(pompa) =2V))/(((∆h)/(∆t))_(V_(pompa) =10V) -((∆h)/(∆t))_(V_(pompa) =2V))

konstanta=c_(FT) =V_(FT t=120s) -((A_(tabung))/(m_(FT)))((∆h)/(∆t))_(t=120s)

Berdasarkan tabel diatas, substitusi untuk tiap variasi pompa diperoleh

V_(pompa) | V_(FT) (volt) | (∆h)/(∆t)(mm/ms)
2V | 2.4011 | 6.0358×10^(-4)
4V | 3.9197 | 0.001
6V | 5.2441 | 0.0014
8V | 6.3062 | 0.0017
10V | 6.8518 | 0.0018

Gambar 3.3 Respon tegangan flow meter V_(FT) terhadap laju level tangki ( ∆h/∆t ).

Dengan menggunakan rumus diatas diperoleh persamaan garis untuk flow:

(A_(tabung))/(m_(FT))=(6.8518-2.4011)/(0.0018-6.0358×10^(-4))=3666(Volt)/(mm/ms)

c_(FT) =6.8518-(3666)(0.0018)=0.253 volt

Substitusikan ke persamaan V_(FT) (dh/dt) :

V_(FT) ((dh)/(dt))=3666×(dh)/(dt)+0.253

Konstanta c_(FT) ini dapat diabaikan karena nilainya terlampau kecil dibandingkan range V_(FT) .

Diketahui A_(tabung) =πr_(tabung)^2 =8100π mm^2

(A_(tabung))/(m_(FT))=G_(FT) =3666

m_(FT) =(A_(tabung))/3666=(8100π)/3666=6.9408(mm^3)/(Volt. ms)

Maka diperoleh model flow meter untuk mengkonversi flow rate (lt/min) ke tegangan output V_(FT) di dalam mikrokontroller sebagai

Q_(in) =m_(FT) V_(FT) dalam (mm^3)/(ms)

Q_(in) =m_(FT) V_(FT) (6×10^(-2) ) dalam lt/min

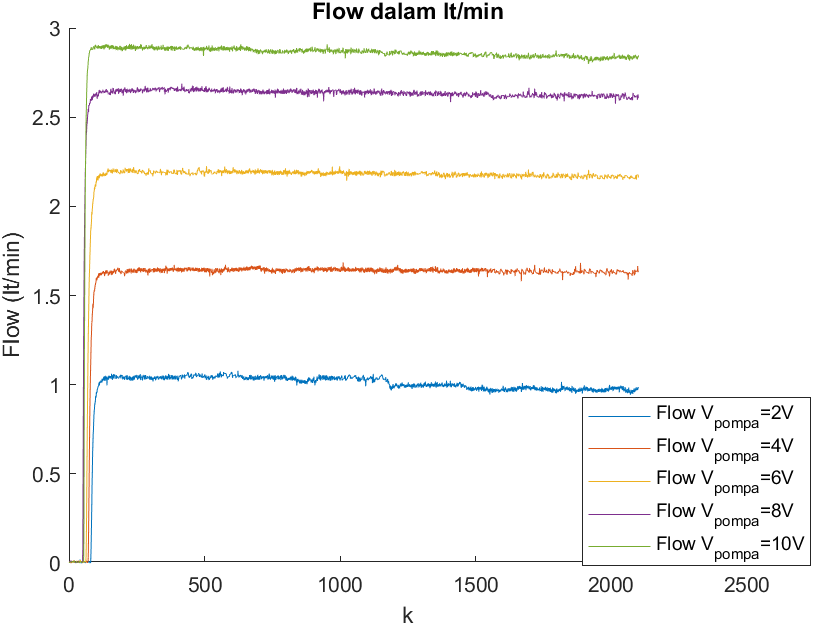
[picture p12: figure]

Gambar 4.4 Respon pembacaan flow meter terhadap variasi tegangan pompa setelah substitusi nilai gain m_(FT)

Model instrumen flow meter dengan input besaran fisis Q_(in) dan output V_(FT) diperoleh sesuai rumusan Berikut.

V_(FT) (h)=(A_(tabung))/(m_(FT))(∆h)/(∆t)

Misalkan model flowmeter adalah G_(FT) =(A_(tabung))/(m_(FT)) , model instrument flowmeter menjadi

V_(FT) (h)=G_(FT) (∆h)/(∆t)

Dimana G_(FT) =(A_(tabung))/(m_(FT))=3666(Volt)/(mm/ms)

#### 2.3.1.3 Permodelan Flow Control Valve

Berdasarkan variasi tegangan valve pada pengambilan data yang telah dilakukan, diperoleh waktu dan flow saat 33% dan 70% steady state yang tersaji dalam tabel Berikut.

Tabel 3.1. Parameter vitechkova tiap variasi tegangan valve ( V_(FC) )

No. | Vfc | y_(ss) | y_33 | t_33 | y_70 | t_70
1 | 13V | 1.7899 | 0.5907 | 0.0025 | 1.2529 | 0.0052
3 | 15V | 2.5560 | 0.8435 | 0.0023 | 1.7892 | 0.0043
4 | 18V | 2.9134 | 0.9614 | 0.0025 | 2.0394 | 0.0052
5 | 21V | 3.0639 | 1.0111 | 0.0014 | 2.1447 | 0.0022

Nilai t_33 dan t_70 digunakan untuk menghitung T_(dV1) dan τ_(V2) sesuai persamaan xx kemudian diperoleh MSE terbaik.

Tabel 3.2. Model vitechkova tiap variasi tegangan valve ( V_(FC) )

No. | Vfc | Kv1 | T_(dv1) | τ_(V1) | G(s) | MSE
1 | 13V | 0.1377 | 0.0012 | 0.0033 | 0.1377/(0.0033s+1)e^(-0.0012s) | 0.3849
3 | 15V | 0.1704 | 0.0013 | 0.0025 | 0.1704/(0.0025s+1)e^(-0.0013s) | 1.2362
4 | 18V | 0.1619 | 0.0011 | 0.0034 | 0.1619/(0.0034s+1)e^(-0.0011s) | 0.8319
5 | 21V | 0.1459 | 9.6676e-04 | 0.001 | 0.1459/(0.001s+1)e^(-0.000967s) | 8.1376

Model terbaik dipilih dengan syarat memiliki MSE kecil dan tidak terpengaruh pressure switch. Model Vfc=13V memiliki MSE kecil namun terpengaruh pressure switch (batas tegangan valve mulai terbuka, pressure switch pompa masih aktif). Model Vfc=18V dipilih selain MSE nya kecil, juga tidak terpengaruh pressure switch.

G_(valve) =0.1619/(0.0034s+1)e^(-0.0011s)

Model ini diubah menjadi sistem orde 2 dengan pendekatan pade, yakni

e^(-Ls) =(e^(- (Ls)/2))/(e^((Ls)/2))=(1-(Ls)/2)/(1+(Ls)/2)

Substitusikan ke G_(valve)

G_(valve) =0.1619/((0.0034s+1)) ((-0.00055s+1))/((0.00055s+1))

#### 2.3.1.4 Permodelan Tangki

Mencari A_O untuk motor drain valve ( A_(O mov) ) dilakukan pada V_(pompa) =3.5V, V_(fc valve) =15V, motor valve full open, dan manual valve tertutup.

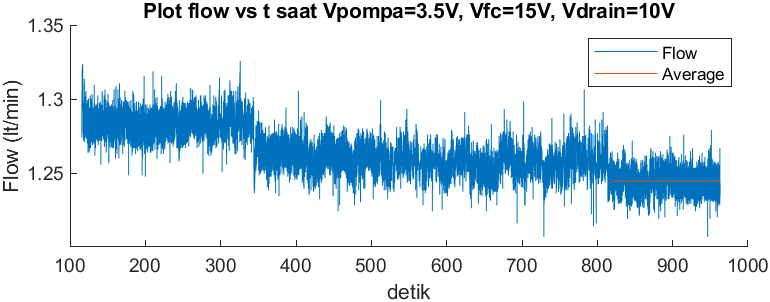
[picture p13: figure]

Berdasarkan respon kurva motor valve di atas saat h=0 diperoleh Q_(in ss) dan h_(ss) .

Q_(in ss mov) =1.2446(lt)/(min)=2.0744×10^(-5) (m^3)/s

h_(ss mov) =49.0878 mm=0.0491 m

Substitusi untuk mendapat A_(O mov) :

A_(O mov) =(2.0744×10^(-5))/(√(2 (9.8) (0.0491)))=2.1148×10^(-5) m^2

Mencari A_O untuk manual drain valve ( A_(O man) ) dilakukan pada V_(pompa) =2.5V, V_(fc valve) =15V, manual valve full open, dan motor valve tertutup.

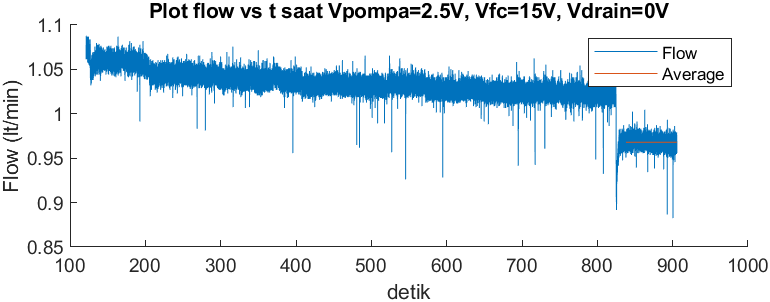
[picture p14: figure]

Berdasarkan respon kurva manual valve di atas saat h=0 diperoleh Q_(in ss) dan h_(ss) .

Q_(in ss man) =0.9679(lt)/(min)=1.6132×10^(-5) (m^3)/s

h_(ss man) =61.651 mm=0.0617 m

Substitusi untuk mendapat A_(O man) :

A_(O man) =(1.6132×10^(-5))/(√(2 (9.8) (0.0617)))=1.4675×10^(-5) m^2

Untuk mevalidasi luasan bukaan kedua valve merupakan jumlahan dari tiap valve, diuji dengan membuka kedua valve dan menghitung luasan A_(O total) .

A_(O 2valve) =A_(O mov) +A_(O man)

Mencari A_O untuk bukaan kedua valve ( A_(O 2valve) ) dilakukan pada V_(pompa) =10V, V_(fc valve) =15V, dan kedua valve terbuka.

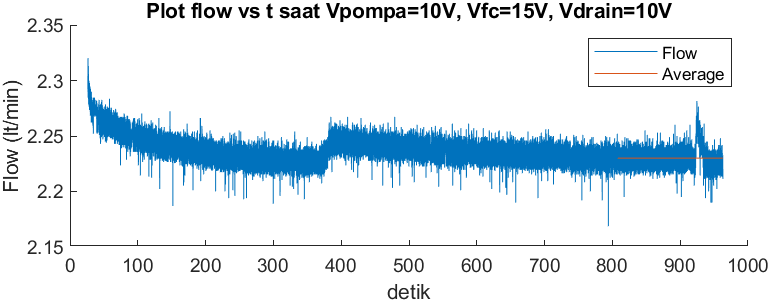
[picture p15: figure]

Berdasarkan respon kurva motor valve di atas saat h=0 diperoleh Q_(in ss) dan h_(ss) .

Q_(in ss 2valve) =2.2301(lt)/(min)=3.7169×10^(-5) (m^3)/s

h_(ss 2valve) =57.7125 mm=0.0577 m

Substitusi untuk mendapat A_(O 2valve) :

A_(O 2valve) =(3.7169×10^(-5))/(√(2 (9.8) (0.0577)))=3.4947×10^(-5) m^2

Untuk membandingkannya, jumlahkan A_(O man) dan A_(O mov)

A_(O mov) +A_(O man) =(2.1148+1.4675) 10^(-5) =3.5823×10^(-5) m^2

Jumlahan ini mendekati nilai A_(O 2valve) , yakni berselisih 0.0876×10^(-5) m^2 sehingga disimpulkan model yang diperoleh sudah benar. Pada kondisi ketika 2 valve dibuka ini, nilai flow keluar maksimum diperoleh, yakni

Q_(out 2valve max) =Q_(in ss 2valve) =2.2301(lt)/(min)=3.7169×10^(-5) (m^3)/s

Model transfer function h/Qin

(h(t))/(Q_(in) (t))=b/(s+a(t))

Diketahui r_(tangki) =90 mm, r_(pipa) =3.85 mm,

b=1/(A_(tangki))=1/(πr_(tangki)^2)

b=1/(π (90/1000)^2)=39.2975 m^(-2)

a(t)=(A_O √(2g))/(A_(tabung) √h)

Tabel Berikut menunjukkan dampak variasi beban terhadap nilai pole a(t) dan model level.

No. | Kondisi | | Pole a(t) | Model h/Q_(in)
| Manual Valve | Motor Valve
1 | Full closed | Full open | 0.0166 | 39.2975/(s+0.0166)
2 | Full open | Full closed | 0.01028 | 39.2975/(s+0.01028)
3 | Full open | Full open | 0.0253 | 39.2975/(s+0.0253)

### 2.3.2 Perancangan Sistem Tertanam

Sistem tertanam merujuk pada sistem computer yang didesain untuk menjalankan tugas atau fungsi tertentu dalam satu unit tunggal. Desain sistem tertanam meliputi perancangan hardware dan software. Desain sistem dimulai dengan mendefinisikan kebutuhan dari fungsi alat dan rangkaian yang sesuai untuk menyelesaikan kebutuhan. Berikut merupakan kebutuhan dan jenis rangkaian yang sesuai.

Tabel 4.2 Kebutuhan sistem dan rangkaian yang sesuai.

No. | Kebutuhan | Rangkaian yang sesuai
1. | Pembacaan tegangan sensor (level dan flow) | ADC dengan voltage divider
2. | Eksekusi linear actuator (flow valve dan motor drain valve) | Operational amplifier dan mosfet regulator
3. | Pemprosesan algoritma kontrol | Mikrokontroller
4. | Switching ON/OFF sinyal referensi (yang dijaga tetap saat mulai running) | Isolator dan relay
5. | Penyimpanan data | MicroSD data logger
6. | Monitoring melalui PC | UART TTL Communication

Berdasarkan tabel di atas, desain rangkaian dapat dibagi menjadi 3 bagian, yakni desain mikrokontroller, desain ADC dan data logger, serta desain penggerak actuator.

#### 2.3.2.1 Desain Mikrokontroller

Gambar 4.4. Modul power supply, mikrokontroller, dan USB-TTL

Mikrokontroller merupakan unit pemprosesan digital yang menjalankan komputasi digital sesuai algoritma fungsi yang diberikan. Input program dapat berasal dari tegangan pembacaan sensor melalui ADC atau informasi yang dikirimkan PC melalui komunikasi UART pada USB-to-TTL adapter. Output hasil program dikirimkan menuju actuator melalui protocol I2C DAC sekaligus disimpan dalam file pada microSD melalui protocol SPI. Supply mikrokontroller dan keseluruhan modul diberikan oleh voltage regulator LM2596 yang dapat menyuplai tegangan 5VDC hingga 3A.

Signal conditioning berupa rangkaian pembagi tegangan diberikan agar tegangan output sensor (0-10VDC) dapat dibaca ADC pada range kerjanya (0-3.3VDC). Pembagi tegangan menggunakan rangkaian seri resistor dan adjustable trimmer.

Gambar 4.5. Rangkaian penurun tegangan ADC dan microSD logger

Hambatan resistor pada rangkaian di atas dapat dihitung menggunakan rumus pembagi tegangan Berikut.

(V_(out))/(V_(in))=(R_17)/(R_17 +R_14 +R_16 +R_12)

Agar tegangan keluaran V_(out) =3.3V, rasio V_(out) /V_(in) ditentukan bernilai (V_(out))/(V_(in))=(3.3V)/(10V)≈1/3 . Hambatan resistor ditetapkan R_16 =R_17 =1kΩ, R_14 =220Ω . Resistansi trimmer diperoleh dengan substitusi nilai tersebut ke persamaan pembagi tegangan.

1/3=(1k)/(1k+1k+220+R_12)

R_12 =780Ω

#### 2.3.2.2 Desain Penggerak Aktuator

Aktuator yang digunakan memiliki range tegangan berbeda. Actuator mendapat sinyal kontrol 12bit dari mikrokontroller, kemudian oleh IC DAC MCP4725 diubah menjadi tegangan 0-5V. Sinyal I2C perlu diisolasi agar MCP4725 tidak menyebabkan drop voltage pada mikrokontroller. Keluaran DAC ini perlu dikuatkan oleh rangkaian non-inverting opamp sehingga menghasilkan 0-10V atau 0-24V. Agar dihasilkan sinyal yang linear dan stabil dibutuhkan regulator power mosfet yang difeedback melalui voltage follower opamp.

No. | Aktuator | Range Input
1. | Flow control valve | 0-24VDC (max current 1A)
2. | Motor drain valve | 0-10VDC
3. | Pompa | 0-10VDC

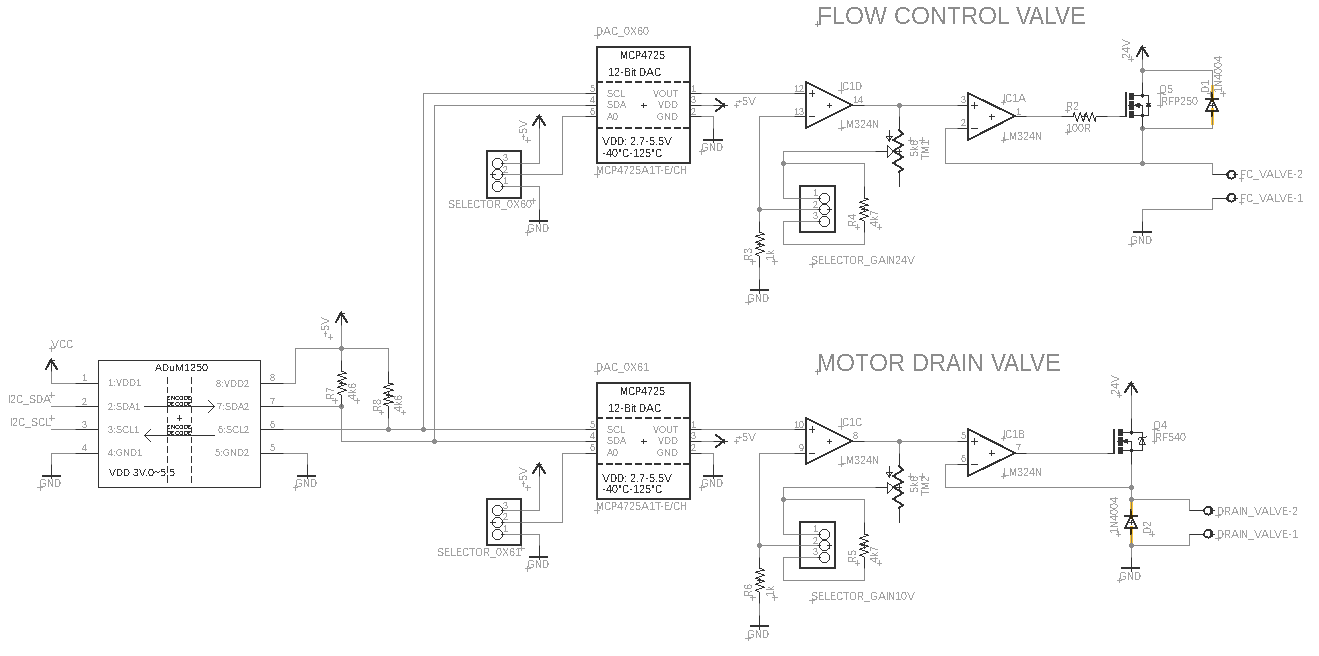
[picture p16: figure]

Gambar 3.6. Rangkaian DAC dan penguatannya

Penguatan opamp flow control valve dihitung berdasarkan rumus Berikut.

(V_(out flow valve))/(V_(in DAC flow valve))=1+(TM_1)/(R_3)

Substitusi parameter kondisi tegangan maksimum untuk mendapat resistansi trimmer TM_1 . V_(out flow valve max) =24V, V_(in DAC flow valve max) =5V, R_3 =1kΩ

24/5=1+(TM_1)/(1k)

19/5=(TM_1)/(1k)

TM_1 =3.8k

Sedangkan, penguatan opamp motor drain valve dihitung berdasarkan rumus Berikut.

(V_(out drain valve))/(V_(in DAC drain valve))=1+(TM_2)/(R_6)

Substitusi parameter kondisi tegangan maksimum untuk mendapat resistansi trimmer TM_2 .

V_(out drain valve) =10V, V_(in DAC drain valve) =5V, R_6 =1kΩ

10/5=1+(TM_2)/(1k)

1=(TM_2)/(1k)

TM_2 =1kΩ

Actuator pompa digerakkan oleh supply tegangan eksternal 0-10V. Tegangan eksternal ini oleh mikrokontroller hanya memiliki 2 kondisi, yakni OFF (0V) dan ON (tegangan eksternal). Relay diberikan sebagai switch yang digerakkan oleh pin digital GPIO mikrokontroller.

Gambar 3.7. Rangkaian switching relay pompa

### 2.3.3 Perancangan Kontroller

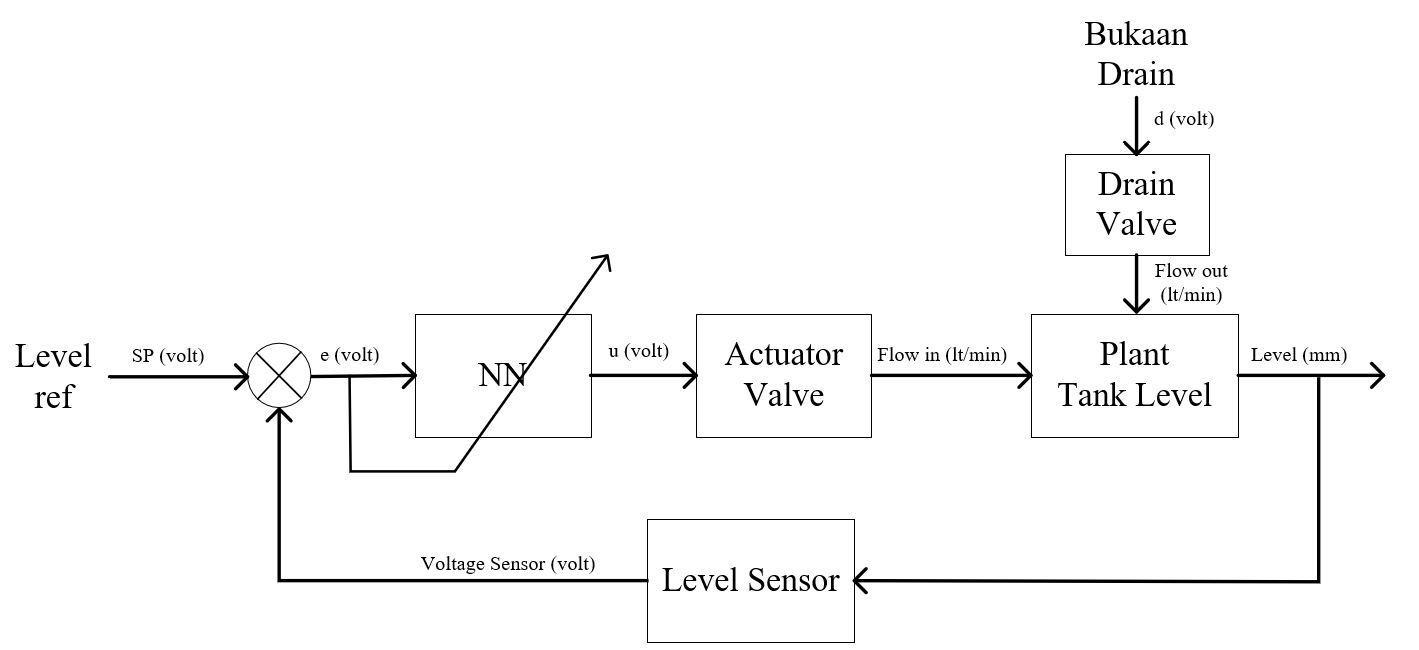
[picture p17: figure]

Gambar 3.44. Diagram blok sistem

Berdasarkan plant dan closed loop diagram diatas, variable proses dapat diidentifikasi. Controlled variables (CVs) merupakan variable proses yang akan dikontrol, pada penelitian ini variable ini adalah level tangki. Nilai yang diinginkan dari variable kontrol ini dinamakan set point. Manipulated variable (MVs) merupaka variable proses yang dapat disesuaikan untuk menjaga controlled variables mendekati set point, variable ini yaitu tegangan flow control valve. Disturbance variables merupakan variable proses yang berdampak controlled variable namun tidak dapat dimanipulasi oleh sistem kontrol. Disturbance berupa beban bukaan drain valve dapat berubah sepanjang interval waktu.

#### 2.3.3.1 Desain dan Perancangan Direct Neural Network

Gambar xx. Struktur Kontroller Direct Neural Network

Struktur neuron pada input layer ditentukan berdasar jumlah orde pada kontroller PID diskrit. Pendekatan ini mengasumsikan kontroller NN yang dibangun memiliki orde time shifting ( z^(-1) ) yang sama dengan PID. Transfer function kontinu kontroller PID diberikan oleh persamaan Berikut.

G(s)=K_P +(K_I)/s+sK_D

Suku derivative dan integral didekati dengan substitusi backward euler agar menjadi PID diskrit.

G(z)=K_P +(T_s)/2(z+1)/(z-1)K_I +(z-1)/(z T_s)K_D

2T_s z(z-1)G(z)=K_P 2T_s z(z-1)+K_I T_s^2 z(z+1)+K_D 2(z-1)

2T_s (1-z^(-1) ) G(z^(-1) )=2T_s K_P (1-z^(-1) )+K_I T_s^2 (1+z^(-1) )+2K_D (z^(-1) -z^(-2) )

Dari persamaan tersebut diketahui bahwa orde maksimum dari transfer function diskrit PID ialah z^(-2) atau berlaku time shifting k-2 . Akibat dasar ini, disusun 3 neuron pada input layer yang masing-masing neuronnya ialah time shifting sekali terhadap data error sebelumnya, yaitu e(k), e(k-1), dan e(k-2) . Selain itu jumlah neuron hidden layer juga berjumlah sama dengan input layer, yakni 3 neuron. Hal ini dipilih agar komputasi perkalian matriks weight lebih mudah. Karena sistem yang dikontrol merupakan sistem SISO, output layer neural network hanya memiliki 1 neuron output untuk memberikan sinyal kontrol ke flow valve.

Inisiasi weight neural network baik input layer ke hidden layer maupun hidden layer ke output layer, diberikan nilai random float 0 hingga 1. Propagasi maju menghasilkan nilai neuron hidden dan output berdasarkan weight sinaps (hubungan neuron antar layer). Sedangkan propagasi balik menghasilkan bobot updating weight input layer dan hidden layer. Updating ini dipengaruhi oleh local gradient hidden ( δ^2 ) dan local gradient output ( δ^1 ) yang merupakan turunan dari cost function error (minimalisasi error).

Pseudocode direct neural network:

1. Initiate w_input, v_hidden = random
2. Initiate learning_rate, alpha
3. x_input = [e(k), e(k-1), e(k-2)]
4. for j=1:3

neuron_hidden(j) = sigmoid(w_input*x)

end

5. neuron_output = sigmoid(v_hidden*neuron_hidden)
6. learning_rate = learning_rate + alpha*abs(e(k))
7. gradient hidden: delta1 = e(k)*neuron_output*(1 – neuron_output)
8. for j=1:3

v_hidden(j) = v_hidden(j) + learning_rate*delta1*neuron_hidden

gradient input: delta2(j) = delta1*v_hidden(j)*neuron_hidden*(1 – neuron_hidden)

for i=1:3

w_input(j,i) = w_input(j,i) + learning_rate*delta2(j)*x_input

end

end

9. updating previous error e(k-2) = e(k-1), e(k-1) = e(k)

#### 2.3.3.2 Skenario Pengujian Kontroller

Pengujian kontroller dilakukan melalui simulasi pada software Simulink dan implementasi langsung pada plant. Respon yang ingin diperoleh dari pengujian kontroller diantaranya pengujian pada kondisi berbeban tanpa alpha, pengujian pada kondisi berbeban dengan alpha, pengujian terhadap tracking setpoint. Proses simulasi dan implementasi dilakukan dengan beberapa konfigurasi plant. Kondisi nominal diartikan sebagai kondisi normal yang mungkin bagi controlled variable mencapai suatu set point. Beban disebut beban nominal terjadi saat berada pada kondisi sistem nominal. Berikut merupakan kondisi nominal dan pembebanan plant PCT-100 untuk pengujian.

Kondisi nominal:

a. Masukan flow rate Q_(in) : 0 – 3 lt/min
b. Tegangan pompa konstan : 10VDC
c. Range tegangan flow control valve : 12VDC (full closed) – 22VDC (full open)
d. Batas run time sistem : 120 detik
e. Time sampling : 50ms
f. Learning rate awal : 10^(-5)
g. Set point level = 100 mm
h. Pembebanan nominal katup terbuka: manual drain valve (full open)

Kondisi pembebanan dengan variasi bukaan valve:

  a. Katup terbuka dengan motor valve terbuka 25%
  b. Katup terbuka dengan motor valve terbuka 50%
  c. Katup terbuka dengan motor valve terbuka 75%
  d. Katup terbuka dengan motor valve terbuka 100%

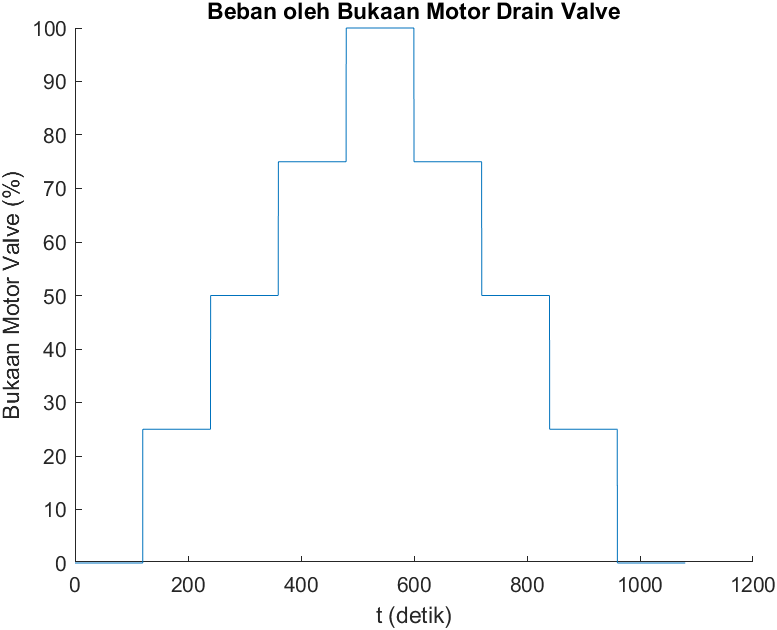
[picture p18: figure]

Gambar ww. Kurva pembebanan uji bukaan drain valve (0% full closed, 100% full open)

Gambar di atas bila diubah menjadi fungsi singularity dengan per periode step 120 detik diperoleh sebagai Berikut.

A_(o mov) (k)={, , 0 , 0s<t<120s, 0.25 , 120s<t<240s, 0.5 , 240s<t<360s, 0.75 , 360s<t<480s, 1 , 480s<t<600s, 0.75 , 600s<t<720s, 0.5 , 720s<t<840s, 0.25 , 840s<t<960s, 0 , 960s<t<1080s

A_(o mov) (k)=0.5 u(k-120)+0.5 u(k-240)-0.5 u(k-360)-0.5 u(k-480)

Selain diberikan variasi pembebanan, dipelajari pula respon kontroller terhadap peningkatan dan penurunan set point. Tracking set point dilakukan dengan memberikan sinyal step level sebagai referensi. Sinyal step ini berada pada range pembacaan level sensor, yakni 42mm hingga 217mm. Berikut merupakan sinyal step tracking set point.

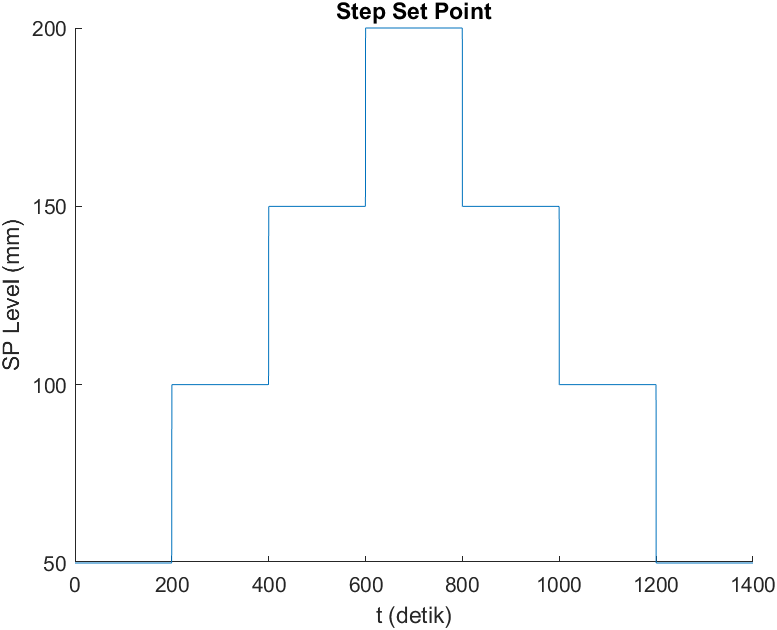
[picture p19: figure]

Gambar ww. Kurva uji tracking set point level

Berdasarkan kurva uji tracking set point diatas dapat ditulis persamaan singularity sebagai Berikut.

SP(k)={, , 50 , 0s<t<200s, 100 , 200s<t<400s, 150 , 400s<t<600s, 200 , 600s<t<800s, 150 , 800s<t<1000s, 100 , 1000s<t<1200s, 50 , 1200s<t<1400s

A_(o mov) (k)=0.5 u(k-120)+0.5 u(k-240)-0.5 u(k-360)-0.5 u(k-480)

Berikut merupakan scenario variasi pengujian yang dilakukan.

1. Pengujian rangkaian ADC dengan sinyal ramp
2. Pengujian rangkaian penggerak actuator dengan sinyal ramp
3. Pengujian kontroller pada kondisi beban berubah tanpa kontroller
4. Pengujian kontroller pada kondisi beban berubah menggunakan kontroller PID ziegler nichols
5. Pengujian kontroller pada kondisi beban berubah dengan learning rate konstan
6. Pengujian kontroller pada kondisi beban berubah dengan learning rate adaptif
7. Pengujian kontroller beban konstan 50% terhadap tracking set point

# BAB 3 Hasil dan Pembahasan

## 3.1 Hasil Penelitian

Tahapan pengujian kontroller merupakan Langkah validasi terhadap desain kontroller yang telah dirancang. Pengujian kontroller terdiri atas 2 tahap, yakni pengujian rangkaian (hardware tertanam) dan pengujian algoritma kontroller (program). Pengujian rangkaian digunakan untuk mengetahui performa hardware yang dirancang, yang meliputi pengujian rangkaian ADC dan rangkaian penggerak actuator. Sementara itu, pengujian algoritma kontroller ditujukan untuk mengetahui performa kontroller terhadap beberapa variasi tujuan kontrol (pembebanan dan tracking set point). Pengujian algoritma kontroller terdiri atas pengujian dalam kondisi beban berubah dan beban konstan. Pengujian beban berubah meliputi pengujian tanpa kontroller, pengujian dengan kontroller PID ziegler nichols, pengujian dengan learning rate konstan, pengujian dengan learning rate adaptif, serta pengujian terhadap tracking set point.

### 3.1.1 Pengujian rangkaian ADC dengan sinyal ramp

Pengujian rangkaian ADC kontroller tertanam dilakukan dengan memberikan sinyal ramp naik selama 60 detik dilanjutkan turun selama 60 detik pada perangkat data actuisition sebagai power supply tegangan referensi. Advantech USB-4716 dipilih karena memiliki keluaran analog output 0-10VDC. Tegangan output ini kemudian dihubungkan ke rangkaian ADC untuk bahan evaluasi performa ADC.

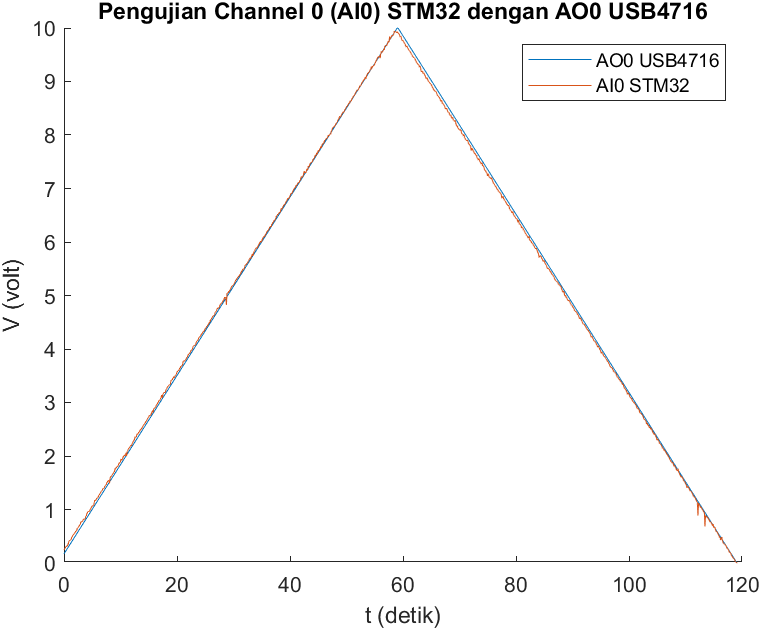
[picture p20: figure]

Gambar xx. Respon bacaan AI channel 0 STM32 terhadap output AO USB4716 (0-10V)

Gambar xx. Respon bacaan AI channel 1 STM32 terhadap output AO USB4716 (0-10V)

### 3.1.2 Pengujian rangkaian penggerak actuator dengan sinyal ramp

Pengujian rangkaian penggerak actuator dilakukan dengan memberikan sinyal ramp naik selama 60 detik kemudian turun 60 detik dalam program mikrokontroller STM32. Pembacaan dilakukan oleh analog input dari modul data actuisition USB-4716 karena memiliki range tegangan 0-10VDC. Terdapat rangkaian penggerak flow control valve (0-24VDC) dan drain valve (0-10VDC) keduanya diuji dan sinyal output dievaluasi.

Rangkaian voltage divider perlu ditambahkan untuk menurunkan tegangan penggerak actuator (24VDC maksimal) menjadi 10VDC maksimal pembacaan AI USB4716. Perhitungan didasarkan rumus pembagi tegangan Berikut dan diperoleh resistansi tiap resistor.

V_(AI USB4716) =V_(AO F.Valve) *(R_2)/(R_1 +R_2)

V_(AI USB4716) =V_(AO F.Valve) *(R_2)/((R_(1 resistor) +R_(1 trimmer) )+R_2)

Dimana R_2 =982 Ω, R_(1 res) =993 Ω, dan R_(1 trimmer) =193.3 Ω

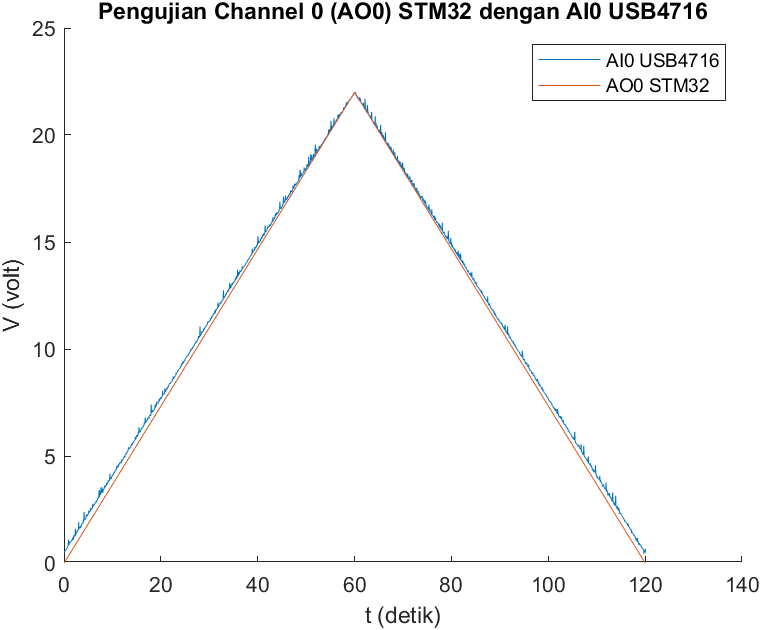
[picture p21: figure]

Gambar xx. Respon bacaan AI USB4716 terhadap output AO channel 0 STM32 (0-22V)

Gambar xx. Respon bacaan AI USB4716 terhadap output AO channel 0 STM32 (0-10V)

### 3.1.3 Pengujian pada kondisi berbeban tanpa kontroller

Pengujian sistem tanpa kontroller dilakukan untuk mengetahui respon level tanpa metode kontrol. Pengujian ini dilakukan closed loop, dimana system diberikan referensi level set point flow control valve yang tetap, yaitu 100mm. Pengujian ini langsung melewatkan sinyal error volt menjadi sinyal kontrol tegangan flow valve.

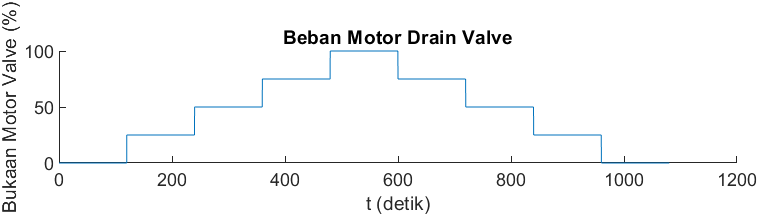
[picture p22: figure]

### 3.1.4 Pengujian pada kondisi berbeban menggunakan kontroller PID ziegler Nichols

Ziegler dan Nichols merumuskan aturan dalam menentukan nilai gain proporsional Kp, waktu integrator Ti, dan waktu derivative Td berdasarkan karakteristik respon transien. Terdapat 2 metode ziegler Nichols. Metode ziegler Nichols kedua dipilih karena plant level memiliki komponen integrator (1/s) . Pada kondisi ini diatur T_i =∞ dan T_d =0 sehingga hanya bekerja kontroller proporsional. Peningkatan Kp dari 0 menuju nilai kritis K_(cr) akan menyebabkan respon berosilasi.

Untuk mencari parameter PID, digunakan transfer function level pada beban nominal (standar), yakni hanya manual valve full open. Model linier plant dapat dirumuskan dalam persamaan Berikut.

G_(flow valve) =

G_(level tangki) =

y_(level sensor) (t)=0.057h(t)+

Dari model plant ini, transfer function gabungan dianalisa menggunakan root locus dan diperoleh pole dan gain complex conjugate. Kurva root locus ditampilkan pada gambar dibawah.

Gambar xx. Kurva root locus model linear plant

Berdasarkan kurva respon tersebut, dipilih critical gain K_(cr) =81.4

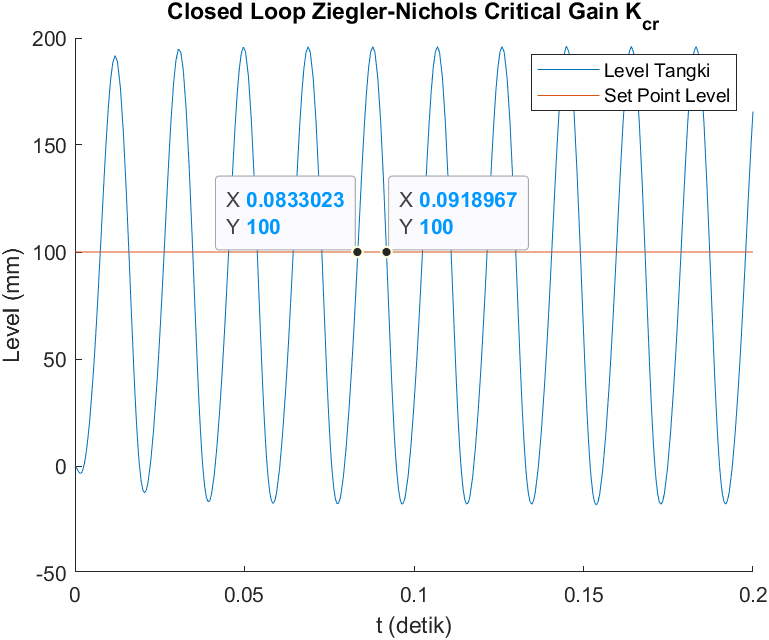
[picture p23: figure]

P_(cr) =0.00938

### 3.1.5 Pengujian pada kondisi berbeban dengan learning rate konstan

Pengujian berbeban dengan learning rate konstan ditujukan untuk mengetahui pengaruh variasi learning rate terhadap respon level air. Pada pengujian ini digunakan pada set point level tetap 100mm dan variasi learning rate konstan, yaitu 0.001, 0.01, 0.1, 1, 2, dan 5. Setiap pengujian diberikan beban motor drain valve 25%, 50%, 75%, dan 100%.

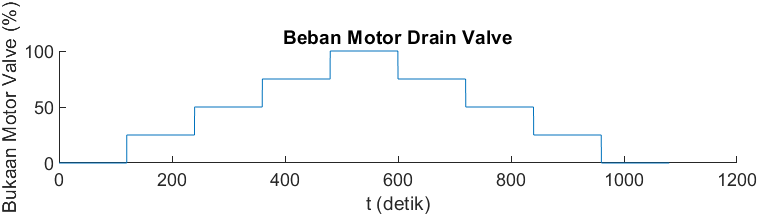
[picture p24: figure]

1. Variasi learning rate konstan η=0.001
2. Variasi learning rate konstan η=0.01
3. Variasi learning rate konstan η=0.1
4. Variasi learning rate konstan η=1
5. Variasi learning rate konstan η=2

Dari pengujian berbeban dan learning rate konstan diatas spesifikasi settling time, persen overshoot, dan steady state value.

No. | η_(konstan) | Settling time (detik) | % overshoot | Yss
1 | 0.001 | 1064 (naik lagi) | 28.0714 (naik lagi) | Naik lagi
2 | 0.01 | 1067.8 (naik lagi) | 27.7318 (naik lagi) | Naik lagi
3 | 0.1 | 1064.2 (naik lagi) | 24.4079 (naik lagi) | Naik lagi
4 | 1 | 291.4078 | 20.7992 (steady) | Steady SP
5 | 2 | 136.2574 | 19.7675 (steady)

### 3.1.6 Pengujian pada kondisi berbeban dengan adaptif learning rate

Pengujian berbeban dengan adaptasi learning rate dilakukan untuk mengetahui respon sistem jika learning rate terus berubah sebanding dengan error sistem. Learning rate awal diberikan 10^(-5) dan divariasikan nilai alpha.

Gambar xx. beban bukaan motor drain valve saat pengujian adaptasi alpha

1. Variasi alpha = 0.0001
2. Variasi alpha = 0.001
3. Variasi alpha = 0.01
4. Variasi alpha = 0.1
5. Variasi alpha = 1

### 3.1.7 Pengujian beban 50% terhadap tracking set point

Pada pengujian ini ingin diketahui respon sistem bila diberikan beberapa step sinyal set point. Pola yang dicoba ialah kenaikan dan penurunan sebesar 25mm.

Variasi jumlah neuron hidden layer

Perbandingan dengan PID ziegler Nichols

## 3.2 Pembahasan

# BAB 4 Kesimpulan dan Saran

## 4.1 Kesimpulan

Inti kesimpulan harus ada di bab4, harus menjawab tujuan berdasarkan pengujian bab4, seberapa efektif. Kesimpulan: metode yg efektif untuk menyelesaikan masalah, error berapa, success rate brp. Kesimpulan diberikan kuantitatif, bukan kualitatif (berdasarkan data), brp RMSE, performance index brp

## 4.2 Saran

Dari hasil yg sudah didapat, kira2 sedikit diperbaiki itu apa?, catatan perbaikan. Agar pembaca tidak melakukan kesalahan yg sama. Jgn seperti ini: setelah fuzzy, akan dikembangkan lebih lanjut menggunakan NN. Saran boleh karena sensor tidak sesuai boleh pake sensor spt ini. Boleh nyalahin hardware.

Eg. Training gcolab berbayar, bisa pake laptop/pc,

Jika tidak pake optimal control jgn bicara hasil yg optimum/optimal

# DAFTAR PUSTAKA

# LAMPIRAN

1. Metode Identifikasi
  1.1. Vitechkova orde 1

Model sistem dapat didekati menggunakan model orde 1 dengan time delay. Untuk sistem orde 1, model diformulasikan sebagai Berikut.

G_(V1) (s)=K/(τ_(V1) s+1)e^(-T_(dV1) s)

T_(dV1) =1.498t_33 -0.498t_70

τ_(V1) =1.245 (t_70 -t_33 )

K=(y_(ss))/u

Dimana t33 dan t70 ialah waktu ketika step response mencapai 33% dan 70%.

No. | Vfc | y_(ss) | y_33 | t_33 | y_70 | t_70
1 | 13V | 1.7899 | 0.5907 | 0.0025 | 1.2529 | 0.0052
3 | 15V | 2.5560 | 0.8435 | 0.0023 | 1.7892 | 0.0043
4 | 18V | 2.9134 | 0.9614 | 0.0025 | 2.0394 | 0.0052
5 | 21V | 3.0639 | 1.0111 | 0.0014 | 2.1447 | 0.0022

No. | Vfc | Kv1 | T_(dv1) | τ_(V1) | G(s) | MSE
1 | 13 | 0.1377 | 0.0012 | 0.0033 | 0.1377/(0.0033s+1)e^(-0.0012s) | 0.3849
3 | 15V | 0.1704 | 0.0013 | 0.0025 | 0.1704/(0.0025s+1)e^(-0.0013s) | 1.2362
4 | 18V | 0.1619 | 0.0011 | 0.0034 | 0.1619/(0.0034s+1)e^(-0.0011s) | 0.8319
5 | 21V | 0.1459 | 9.6676e-04 | 0.001 | 0.1459/(0.001s+1)e^(-0.000967s) | 8.1376

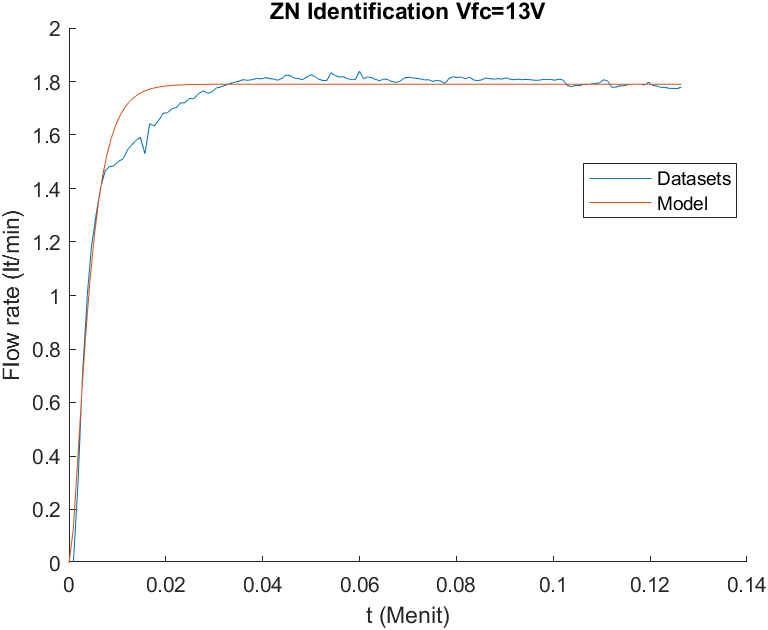
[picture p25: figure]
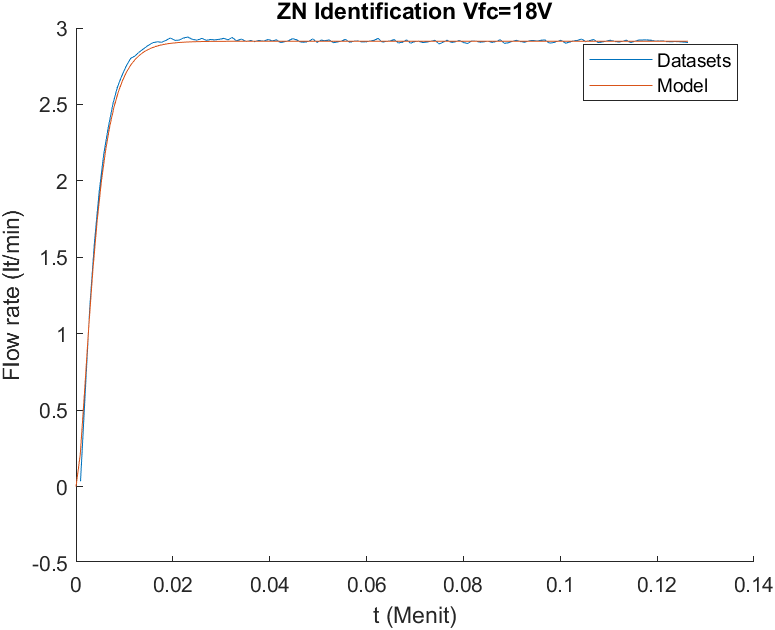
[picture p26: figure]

Seluruh kode program, rangkaian, dan data hasil pengujian dapat diakses pada repository penulis Berikut.

https://github.com/fariszuh/TA-PCT100

# BIODATA PENULIS

Penulis dilahirkan di Madiun, 29 Januari 1985, merupakan anak pertama dari 4 bersaudara. Penulis telah menempuh pendidikan formal yaitu di TK ABA 18 Madiun, SDN Beteng 1 Madiun, SMPN 2 Madiun dan SMAN 2 Madiun. Setelah lulus dari SMAN tahun 2020, Penulis mengikuti SBMPTN dan diterima di Departemen Teknik Mesin FTIRS - ITS pada tahun 2020 dan terdaftar dengan NRP 02112040000130.

Photo closed-up

Di Departemen Teknik Mesin Penulis sempat aktif di beberapa kegiatan Seminar yang diselenggarakan oleh Departemen, Himpunan Mahasiswa Teknik Mesin (HMM) dan aktif sebagai Asisten Praktikum Mesin Konversi Enersi maupun Grader mata kuliah Termodinamika.

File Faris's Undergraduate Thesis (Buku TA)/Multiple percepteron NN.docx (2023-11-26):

Multiple percepteron: 3 hidden layer

Untuk input layer:

S_j =∑_(i=1)^3 w_(ji) x_i

r_j =1/(1+e^(-S_j))

Untuk output layer:

Forward:

r=∑_(l=1)^3 v_l h_l

u=1/(1+e^(-r))

Backward:

(∂E)/(∂v_l)=(∂E)/(∂e_y)(∂e_y)/(∂e_u)(∂e_u)/(∂u)(∂u)/(∂r)(∂r)/(∂v_l)

Dimana ∂u/∂r

(∂u)/(∂r)=(∂{1/(1+e^(-r))})/(∂r)=(e^(-r))/((1+e^(-r) )^2)=u(1-u)

Substitusi:

(∂E)/(∂v_l)=e_y (∂e_y)/(∂e_u) (-1) u(1-u)h_l =-e_y u(1-u)h_l (∂e_y)/(∂e_u)

Updating:

v_l^((t+1)) =v_l^((t)) -η(∂E)/(∂v_l)

v_l^((t+1)) =v_l^((t)) +ηe_y u(1-u)h_l sign((∂e_y)/(∂e_u))

Untuk 3rd hidden layer: l layer

Forward:

S_l =∑_(k=1)^3 w_(lk) h_k

h_l =1/(1+e^(-S_l))

Backward:

(∂E)/(∂w_(lk))=(∂E)/(∂e_y)(∂e_y)/(∂e_u)(∂e_u)/(∂u)(∂u)/(∂r)(∂r)/(∂h_l)(∂h_l)/(∂S_l)(∂S_l)/(∂w_(lk))

Dimana (∂h_l)/(∂S_l)

(∂h_l)/(∂S_l)=(∂{1/(1+e^(-S_l))})/(∂S_l)=h_l (1-h_l )

Substitusi:

(∂E)/(∂w_(lk))=e_y (∂e_y)/(∂e_u) (-1) u(1-u) v_l h_l (1-h_l ) h_k

Updating:

w_(lk)^((t+1)) =w_(lk)^((t)) -η(∂E)/(∂w_(lk))

w_(lk)^((t+1)) =w_(lk)^((t)) +ηe_y u(1-u) v_l h_l (1-h_l ) h_k sign((∂e_y)/(∂e_u))

Untuk 2rd hidden layer: k layer

Forward:

S_k =∑_(j=1)^3 w_(kj) h_j

h_k =1/(1+e^(-S_k))

Backward:

(∂E)/(∂w_(kj))=(∂E)/(∂e_y)(∂e_y)/(∂e_u)(∂e_u)/(∂u)(∂u)/(∂r)(∂r)/(∂h_l)(∂h_l)/(∂S_l)(∂S_l)/(∂h_k)(∂h_k)/(∂S_k)(∂S_k)/(∂w_(kj))

Dimana (∂h_k)/(∂S_k)

(∂h_k)/(∂S_k)=(∂{1/(1+e^(-S_k))})/(∂S_k)=h_k (1-h_k )

Substitusi:

(∂E)/(∂w_(kj))=e_y (∂e_y)/(∂e_u) (-1) u(1-u) v_l h_l (1-h_l ) w_(lk) h_k (1-h_k )h_j

Updating:

w_(kj)^((t+1)) =w_(kj)^((t)) -η(∂E)/(∂w_(lk))

w_(lk)^((t+1)) =w_(kj)^((t)) +ηe_y u(1-u) v_l h_l (1-h_l ) h_k sign((∂e_y)/(∂e_u))

Untuk 1st hidden layer: j layer

Forward:

S_j =∑_(i=1)^3 w_(ji) x_i

h_j =1/(1+e^(-S_j))

Backward:

(∂E)/(∂w_(ji))=(∂E)/(∂e_y)(∂e_y)/(∂e_u)(∂e_u)/(∂u)(∂u)/(∂r)(∂r)/(∂h_l)(∂h_l)/(∂S_l)(∂S_l)/(∂h_k)(∂h_k)/(∂S_k)(∂S_k)/(∂h_j)(∂h_j)/(∂S_j)(∂S_j)/(∂w_(ji))

Dimana (∂h_j)/(∂S_j)

(∂h_j)/(∂S_j)=(∂{1/(1+e^(-S_j))})/(∂S_j)=h_j (1-h_j )

Substitusi:

(∂E)/(∂w_(ji))=e_y (∂e_y)/(∂e_u) (-1) u(1-u) v_l h_l (1-h_l ) w_(lk) h_k (1-h_k ) w_(kj) h_j (1-h_j ) x_i

Updating:

w_(ji)^((t+1)) =w_(ji)^((t)) -η(∂E)/(∂w_(ji))

w_(ji)^((t+1)) =w_(ji)^((t)) +ηe_y u(1-u) v_l h_l (1-h_l ) w_(lk) h_k (1-h_k ) w_(kj) h_j (1-h_j ) x_i sign((∂e_y)/(∂e_u))

Model Level Transmitter

Model Flow Meter

Model Flow Control Valve

Model flow valve diambil dengan memberikan variasi tegangan flow valve dan membandingkan debit keluaran valve. Input tegangan yang diberikan yaitu 10V, 12V, 12.5V, 13V, 14V, 15V, 16V, 17V, 18V, 19V, 20V, 21V, dan 22V.

Prinsip least square yang dinyatakan oleh gauss berbunyi jumlahan dai kuadrat selisih nilai actual dan komputasi, dikalikan jumlah data menyatakan tingkat presisi, harus diminimumkan.

Menghitung gain G_(LT) :


Fssfas


Model Drain Valve

Drain valve merupakan actuator proporsional yang

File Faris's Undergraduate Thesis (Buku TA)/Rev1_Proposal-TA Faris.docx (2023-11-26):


PROPOSAL TUGAS AKHIR – EE184701

PERANCANGAN KONTROLLER ADAPTIF NEURO PID UNTUK PENGATURAN CASCADE LEVEL-FLOW PADA PLANT PCT-100

MUHAMMAD FARIS ZUHAIRI

NRP 07111940000164

Dosen Pembimbing

Eka Iskandar, S.T., M.T.

NIP 198005282008121001

Mohamad Abdul Hady, S.T., M.T.

NIP 198904132015041002

Program Studi Teknik Sistem Pengaturan

Departemen Teknik Elektro

Fakultas Teknologi Elektro dan Informatika Cerdas

Institut Teknologi Sepuluh Nopember

Surabaya

2022

# LEMBAR PENGESAHAN

PERANCANGAN KONTROLLER ADAPTIF NEURO PID UNTUK PENGATURAN CASCADE LEVEL-FLOW PADA PLANT PCT-100

PROPOSAL TUGAS AKHIR

Diajukan untuk memenuhi salah satu syarat

memperoleh gelar Sarjana Teknik pada

Program Studi S-1 Teknik Sistem Pengaturan

Departemen Teknik Elektro

Fakultas Teknologi Elektro dan Informatika Cerdas

Institut Teknologi Sepuluh Nopember

Oleh : MUHAMMAD FARIS ZUHAIRI

NRP. 07111940000164

Disetujui oleh Tim Penguji Proposal Tugas Akhir :

1. | Eka Iskandar, S.T., M.T. | Pembimbing
2. | Mohamad Abdul Hady, S.T., M.T. | Ko-pembimbing
3. | Nama dan gelar penguji | Penguji
4. | Nama dan gelar penguji | Penguji
5. | Nama dan gelar penguji | Penguji

SURABAYA

Desember, 2022

# ABSTRAK

PERANCANGAN KONTROLLER ADAPTIF NEURO PID UNTUK PENGATURAN CASCADE LEVEL-FLOW PADA PLANT PCT-100

Nama Mahasiswa / NRP | : | Muhammad Faris Zuhairi / 07111940000164
Departemen | : | Teknik Elektro FTEIC - ITS
Dosen Pembimbing | : | Eka Iskandar, S.T., M.T. Mohammad Abdul Hady, S.T., M.T.

Abstrak

Saat ini industry proses banyak menerapkan sistem otomasi pengaturan level fluida dalam tangki. Controller cascade PID masih popular dan umum digunakan pada industry. Controller ini unggul karena mampu menahan disturbance dan akurasinya yang tinggi. Namun, controller ini diperlukan manual tuning bila terdapat variasi dan gangguan pada sistem. Dengan adanya dinamika level pada sistem tangki PCT-100, controller yang dirancang harus mampu menyesuaikan sinyal kontrol guna memenuhi spesifikasi respon yang diinginkan. Karakteristik respon level yang diinginkan seperti error steady state dan overshoot yang minimum. Hal ini diharapkan kontroller adaptif neuro PID dengan struktur cascade level-flow memiliki hasil lebih baik dibandingkan PID konvensional.

Kata kunci: Cascade, Level, Neural Network, PCT-100, PID

# ABSTRACT

PERANCANGAN KONTROLLER ADAPTIF NEURO PID UNTUK PENGATURAN CASCADE LEVEL-FLOW PADA PLANT PCT-100

Student Name / NRP | : | Muhammad Faris Zuhairi / 07111940000164
Department | : | Teknik Elektro FTEIC - ITS
Advisor | : | Eka Iskandar, S.T., M.T. Mohammad Abdul Hady, S.T., M.T.

Abstract

At the present, the process industry has implemented the automatic system for liquid level control. Cascade PID controller is still popular and commonly used in industry. However, this controller needs manual tuning if variation and disturbance exist. Based on level dynamics of PCT-100 tank, the controller must be capable of adapting the control signal to fulfill desired response specification. Level response characteristics, such as steady-state error and overshoot must be minimum. Adaptive neuro PID controller with level-flow cascade will be expected to have a better response than conventional PID.

Keywords: Cascade, Level, Neural Network, PCT-100, PID

# DAFTAR ISI

# DAFTAR GAMBAR

# DAFTAR TABEL

# DAFTAR SIMBOL

PENDAHULUAN

## 1.1 Latar Belakang

Saat ini industri proses banyak menerapkan sistem otomasi pengaturan level fluida. Fluida dipompa dan ditampung dalam tangki khusus yang memerlukan pengendalian agar memenuhi batas level yang diperbolehkan. Umumnya level air dianalisis dengan mengestimasi model linear yang merepresentasikan sifat dinamis dari level terhadap titik setimbangnya. Apabila ketinggian cairan tidak dikendalikan maka rantai proses produksi akan terganggu. Jika ketinggian cairan melebihi ketinggian yang diinginkan maka akan terjadi overflow atau cairan akan meluap sehingga mengganggu atau dapat merusak alat-alat lain. Sebaliknya jika ketinggian cairan kurang dari ketinggian yang diinginkan maka proses tidak akan bekerja. Oleh karena itu ketinggian suatu cairan harus dikendalikan dalam suatu industri.

Umumnya dalam industri, fluida dialirkan menggunakan pompa, laju massa diatur dengan control valve, dan ketinggian fluida dalam tangki dibaca oleh level transmitter. Namun, pengaturan level tangki memiliki karakteristik time-varying dan non linier. Kontroller PID membutuhkan parameter berbeda-beda (tuning ulang) untuk menyesuaikan respon yang cepat. PCT-100 merupakan miniatur sistem proses industri yang terdapat fasilitas untuk melakukan pengaturan terhadap empat buah variable kontrol, yaitu flow, level, suhu, dan tekanan. Level pada plant PCT-100 yang dikendalikan seringkali mengalami perubahan parameter dalam kondisi-kondisi tertentu. Untuk mengatasi perubahan ini, diperlukan metode yang dapat belajar (learning) terhadap perubahan (Ghufron, 2016).

Salah satu metode autotuning yang menggunakan algoritma cerdas ialah neural network. Algoritma ini dapat mempelajari perubahan beban pada plant dan akan otomatis melakukan tuning selama plant beroperasi sehingga mudah memenuhi spesifikasi kontrol yang diinginkan. Controller cascade mampu melakukan disturbance rejection dan meningkatkan akurasi sistem (Zhang et al., 2012). Pada tugas akhir ini akan dirancang controller adaptif neuro PID sistem cascade level-flow plant PCT-100 yang meminimalkan error steady state dan overshoot.

## 1.2 Rumusan Masalah

Kontroller PID pada dasarnya bersifat tetap selama parameter P, I, dan D tidak diubah. Ketika terjadi perubahan parameter plant yang diakibatkan oleh pembebanan, terkadang sinyal kontrol yang diberikan tidak sesuai dengan kondisi plant saat ini sehingga muncul pelonjakan atau penurunan nilai. Berdasarkan masalah perubahan parameter tuning tersebut, dirancang kontroller adaptif neuro PID sistem cascade level-flow plant PCT-100 yang meminimalkan error steady state dan overshoot.

## 1.3 Batasan Masalah

Ruang lingkup penelitian ini membahas mengenai pengaturan cascade level-flow pada tangki. Plant yang digunakan ialah PCT-100 dengan pengendalian menggunakan kontroller adaptif neuro PID. Batasan lain yaitu mengabaikan efek temperature dan pressure dalam tangki.

## 1.4 Tujuan

Tujuan yang diharapkan dari tugas akhir ini ialah merancang kontroller adaptif neuro PID sistem cascade level-flow plant PCT-100 yang meminimalkan error steady state dan overshoot.

## 1.5 Manfaat

Manfaat yang ingin didapatkan melalui tugas akhir ini ialah merancang kontroller adaptif neuro PID sistem cascade level-flow plant PCT-100 yang meminimalkan error steady state dan overshoot. Selain itu, diharapkan penelitian ini akan memberikan inovasi terbaru pada metode kontrol PID dengan menggunakan adaptif neural network terhadap variasi pembebanan.

# BAB 1 TINJAUAN PUSTAKA

## 1.1 Hasil Penelitian Terdahulu

Penelitian terdahulu digunakan untuk mengetahui metode dan hasil penelitian yang sudah dilakukan. Penelitian terdahulu diperlukan sebagai landasan dan acuan peneliti terhadap perbandingan dan hubungan antar variable yang diuji.

Penelitian plant PCT-100 oleh Rachmad Dwi Raharjo (2014) dilakukan dengan metode PID gain scheduling terhadap level proses. Identifikasi sistem dilakukan dengan metode Harriot dan divalidasi menggunakan ISE/Integral Square Error. Hasil yang diperoleh yakni kontroller PID gain scheduling dapat mengendalikan respon dinamis dalam simulasi dengan rata-rata error waktu tunak 0.06% dan 0.12% pada implementasi. Namun, nilai gain PID masih dipengaruhi variable tertentu yang berubah kontinu atau dengan kata lain gain scheduling hanya cocok untuk variasi yang terprediksi.

Penelitian level proses kemudian disempurnakan oleh penelitian M. Zakki Ghufron (2016) yang menggunakan self-tuning PID dengan pendekatan adaptif. Kontroller adaptif dapat memperbaiki kelemahan metode gain scheduling, dimana dapat bekerja pada variasi tak terprediksi. Nilai gamma memengaruhi kecepatan adaptasi kontroller self tuning PID. Kriteria square time-square error/STSE unggul karena memberikan error terkecil 3.64% saat simulasi dan 0.093% bila diberikan pembebanan. Namun, implementasinya masih memerlukan waktu learning yang lama dan memerlukan otomatisasi penentuan nilai gamma.

Berdasarkan penelitian PCT-100 sebelumnya, diharapkan desain kontroller PID yang detuning menggunakan metode neural network dapat memberikan waktu yang cepat dalam proses learning.


Gambar x. Training window neuron

Penelitian multilayer neural network oleh (Patel & Kumar, 2015) menyatakan multilayer neuro PID dapat menstabilkan sistem magnetic levitation orde-2 yang unstable dengan settling time kecil dan zero steady state error. Penelitian ini menggunakan 3 jenis layer neural network, yaitu 1 input layer, 1 output layer, dan 10 hidden layer. Hasil menunjukkan kontroller series Neuro PID memiliki settling time lebih kecil daripada conventional PID, zero error steady state, dan overshoot yang kecil. Kelebihan dari penggunaan neuro PID ialah mampu mempertahankan respon seragam plant. Apabila terdapat factor eksternal yang mengganggu respon, neuro PID dapat mengeliminasi factor ini dan menghilangkan error agar respon tetap seragam.

## 1.2 Dasar Teori

### 1.2.1 Sistem Kontrol Proses

Sistem kontrol proses adalah gabungan kerja dari alat-alat pengendalian otomatis. Semua peralatan yang membentuk sistem kontrol disebut instrumentasi kontrol proses. Empat variable proses yang umum pada Industri yaitu temperature, level, flow, dan pressure. Kehandalan produk dan produktivitas menjadi kunci keberhasilan proses industri, sebagaimana kegagalan akan menghasilkan kerusakan produk dalam waktu singkat. Untuk mengukur performansi dalam pengaturan, biasanya dinyatakan dengan ukuran - ukuran waktu naik (τr), waktu puncak (τp), settling time (τs), maximum overshoot (Mp), waktu tunda/delay time (τd), nilai kesalahan, dan damping ratio.

Semua analisa sistem kontrol selalu dimulai dengan menampilkan diagram blok sistem. Di dalam diagram blok sistem akan selalu ada komponen-komponen pokok seperti elemen proses, elemen pengukuran (sensing element dan transmitter), elemen kontroller (control unit), dan final control element (control valve). Dalam bentuk matematis semua blok elemen itu akan diisi persamaan-persamaan matematik yang merupakan fungsi alih elemen-elemen tersebut. Secara umum, diagram blok sistem kontrol dapat dilihat seperti pada Gambar berikut.


Diagram blok semacam ini dapat ditemukan pada hampir semua literatur. Ada literatur lain yang menampilkan kotak-kotak elemen dalam susunan yang berbeda dengan yang ada dalam gambar diatas. Namun pada dasarnya semua cara penggambaran itu sama benarnya, dan cara kerjanya pun tidak berbeda sama sekali. Sebenarnya diagram kotak ini disiapkan untuk analisa matematis. Di dalam Gambar diatas, bagian kontroller mempunyai summing junction dengan tanda positif-negatif (+/-). Di titik inilah Langkah membandingkan dilakukan dengan menggunakan besaran set-point dengan sinyal hasil pengukuran. Hasilnya adalah sinyal kesalahan. Tanda negatif (-) di summing junction membawa arti yang sangat spesifik bagi seluruh sistem. Karena tanda inilah sistem kontrol otomatis juga biasanya disebut dengan umpan balik negatif.

### 1.2.2 Permodelan Plant

Plant PCT-100 yang digunakan tersusun atas instrument inner loop dan outer loop. Instrument inner loop tersusun atas flow transmitter, flow kontroller, dan pompa suplai. Sedangkan, outer loop tersusun atas level transmitter, level kontroller, proportional drain valve, sump tank, dan process tank. Diagram P&ID di bawah menunjukkan instrument pada PCT-100.


Gambar 2.P&ID Plant PCT-100

Sebelum melakukan proses permodelan plant, perlu digambarkan diagram closed loop untuk mendefinisikan fungsi alih dan mempermudah analisis respon. Sesuai dengan diagram P&ID yang akan digunakan, blok diagram berbentuk cascade yang tersusun atas closed loop master (primary/outer) dan slave (secondary/inner). Kontroller cascade populer digunakan karena kontroller ini memiliki kelebihan (Padhan & Majhi, 2012): (1) mampu melakukan reject disturbance yang timbul di inner loop; (2) meningkatkan kecepatan dan akurasi respon sistem; (3) mengurangi efek variasi parameter pada inner loop.

Proses utama (fungsi alih G_(level) ) memiliki single output h yang dikendalikan oleh manipulating single input Qin_tangki (debit masukan tangki) melalui kontroller Clevel. Output h kemudian dikenai disturbance dlevel yang merupakan gangguan white noise <10% terhadap ketinggian tangki h. Gangguan ini disebabkan oleh bukaan dari proportional drain valve. Implementasi cascade control pada slave (inner) kontroller dilakukan oleh pengaturan Qin dengan menyesuaikan pompa sebagai final control element (transfer function G_(flow) ). Pada PCT-100, G_(flow) merupakan hubungan dinamis antara sinyal kontroller C_(flow) dengan Qin_tanki. Set point dari inner kontroller ini ialah Ud atau debit yang diinginkan. Terdapat disturbance d_(flow) berupa white noise sinyal kontrol pompa <10%. Negative feedback inner loop dibaca menggunakan flow transmitter H_(FT) dan outer loop oleh floating type level transmitter H_(LT) .


Gambar 2.1 Struktur Closed Loop Flow-Level

#### 1.2.2.1 Permodelan Pompa

Pemodelan pompa bertujuan untuk mendapatkan nilai penguatan dari pompa yang dilambangkan dengan Kpompa. Pompa merupakan peralatan yang dikenai disturbance d_flow yang akan di-reject kontroller flow dari feedback H_(flow) . Pompa yang digunakan memiliki rating 24 VDC, 0.5A, flow max. 7lt/min (116.667 cm3/s), dan pressure cut off 1.5bar

Q_(pompa) =K_(pompa) (u_(pompa) +d_(flow) )

Q_(pompa) =K_(pompa) u_(pompa) +d_(flow)

Untuk mengidentifikasi nilai Kpompa, dilakukan pengujian open loop dengan memberikan tegangan kontrol u_(pompa) 0-10V dan dihitung lama mencapai titik level yang ditentukan. Secara matematis dapat dirumuskan sebagai berikut.

K_(pompa, OL) =(Q_(pompa,OL))/(u_(pompa))=(V_(diamati))/(t u_(pompa))=A_(tanki) (h_(diamati))/(t u_(pompa))

Diketahui jari-jari tangki proses 8cm, sehingga luas alas tangki dan K_(pompa,OL) diperoleh sebagai berikut.

A_(tangki) =π r^2 =π (8^2 )=201.143 cm^2

K_(pompa, OL) =201.143 (h_(diamati))/(t u_(pompa))

Bila digunakan acuan h_(diamati) =10 cm dan diberikan sinyal step pompa u_(pompa) =10V , dengan stopwatch akan diperoleh nilai t dan K_(pompa,OL) .

K_(pompa, OL) =201.143/t(cm^3)/s

#### 1.2.2.2 Permodelan Pipa

Pemodelan pipa dilakukan untuk mencari besarnya waktu tunda yang diakibatkan oleh panjang pipa. Hubungan waktu tunda dengan panjang pipa dapat dirumuskan pada Persamaan berikut.

θ=(volume pipa (cm^3 ))/(debit yang masuk ke pipa (cm^3 /s))

Jika dihubungkan dengan sistem pengaturan level maka waktu tunda yang terjadi merupakan hubungan antara debit air yang dikeluarkan pompa dan debit air yang masuk ke tangki dituliskan pada Persamaan berikut.

(Q_(in tangki))/(Q_(pompa))=e^(-θs)

#### 1.2.2.3 Permodelan Tangki dan Control Valve

Komponen utama dalam pemodelan tangki adalah tangki itu sendiri dan control valve. Tangki diasumsikan seperti kapasitor dikarenakan sifatnya yang mirip. Ketika proses pengisian air seperti proses pengisian muatan sedangkan proses pembuangan air seperti proses pembuangan muatan pada kapasitor. Oleh sebab itu, kapasitansi tangki dapat didekati dengan luas alas tangki yang berupa lingkaran seperti Persamaan berikut.

A=(perubahan volume air (cm^3 ))/(perubahan ketinggian air (m))=(π d^2)/4

Untuk menjaga flow air masuk dan keluar tanki bernilai sama, digunakan hukum kekekalan massa.

Q_(in tangki) -Q_(out tangki) =Q_(tangki)

Q_(tangki) merupakan laju volume air per satuan waktu atau dapat dirumuskan sebagai

Q_(in tangki) -Q_(out tangki) =A(dh)/(dt)

Adanya control valve memengaruhi jumlah debit volume tangki. Penguatannya dapat diibaratkan sebagai nilai hambatan R, yaitu perubahan debit per tegangan output.

R=(Q_(out tangki))/(u_(valve))

Q_(out tangki) =R u_(valve)

Nilai R dapat ditentukan saat kondisi open loop dengan Q_(in tangki) =0 dan dihitung waktu hingga air tangki habis pada h acuan tertentu.

R=(Q_(out tangki))/(u_(valve))=(A_(tangki) h_(diamati))/(t u_(valve))

Diketahui A_(tangki) =π r^2 =π (8^2 )=201.143 cm^2 , apabila h_(diamati) =10cm saat u_(valve) =10V , dengan mudah didapat nilai R.

R=201.143/t cm^3 /s

Substitusi ke persamaan debit untuk mendapat hubungan dengan h:

Q_(in tangki) -R u_(valve) =C(dh)/(dt)

Dengan menggunakan transformasi laplace, diperoleh transfer function ketinggian tangki terhadap debit masukan. R ialah konstan.

Q_(in tangki) (s)-R U_(valve) (s)=C sH(s)

H(s)=1/(sA)(Q_(in tangki) -R U_(valve) (s))

R(U_(valve) (s))/(sA) disebut disturbance level atau d_(level) (s)=R(U_(valve) (s))/(sA) .

Dengan memasukkan parameter plant ke persamaan transfer function di atas pada tabel berikut, akan diperoleh transfer function tangki. Permodelan keseluruhan plant dapat dihitung sebagai berikut.

H(s)=(Q_(in tangki))/(sA)+d_(level) (s)

H(s)=(Q_(pompa) e^(-θs))/(sA)+d_(level) (s)

H(s)=((K_(pompa) u_(pompa) +d_(flow) ) e^(-θs))/(sA)+d_(level) (s)

#### 1.2.2.4 Permodelan Sensor

Level tranducer yang digunakan bertipe magnetostrictive position sensor. Sensor level (ketinggian) dimodelkan untuk mendapatkan nilai gain penguatan K2. K2 merupakan rasio rentang kerja tegangan terhadap rentang ketinggian air tangki.

K_2 =(rentang tegangan keluaran (V))/(rentang ketinggian air tangki (cm))=(10V)/(18cm)=0.55V/(cm)

Sedangkan, flow tranducer yang digunakan bertipe turbine flow rate sensor. Datasheet dan spesifikasi flow tranducer disajikan pada tabel di bawah (Bytronic, 2015).

Tabel 2.1 Spesifikasi Flow Tranducer

No. | Parameter | Spesifikasi
1 | Operating pressure | 14 bar maximum
2 | Burst pressure | 170 bar
3 | Operating temperature | -20°C to 100°C (ambient +80°C for cable)
4 | Input power | 5 to 24 VDC @ 8mA
5 | Accuracy | ±3% of reading
6 | Repeatability | 0.5% of full scale
7 | Flow range | Litres per minute 0.5 to 5

Dengan mengabaikan efek temperature dan tekanan lingkungan, diperoleh penguatan flow tranducer.

K_f =(rentang tegangan keluaran (V))/(rentang flow rate ((cm2)/s))=(10V)/(5 lt/min)

### 1.2.3 Hardware yang digunakan

#### 1.2.3.1 PCT-100


PCT-100 adalah miniatur sistem pengaturan proses pada dunia industri seperti pada industri makanan dan minuman, industri kimia, pemurnian air, dan pengolahan limbah. PCT-100 merupakan produk dari vendor Bytronic. Perangkat lunak yang mendukung PCT-100 mempunyai fasilitas untuk melakukan pengaturan terhadap empat buah variable kontrol diantaranya debit, level, suhu, dan tekanan.

Tujuan dari PCT-100 adalah untuk memberikan pembelajaran yang mencerminkan masalah pengaturan sebuah sisem sebenarnya dalam dunia industri, mempermudah untuk melakukan analisis dan menerapkan metode kontrol yang lain. PCT-100 juga dapat digunakan untuk menggambarkan secara sederhana dan jelas, karakteristik dari kontroller P, I, dan D. Beberapa sasaran PCT-100 antara lain memberikan keuntungan yang dalam hal penerapan pengaturan berbasiskan mikroprosesor untuk proses otomasi, menyediakan proses skala kecil dengan gambaran masalah yang ditemukan dalam dunia industri sehingga dapat diterapkan teknik kontrol yang berbeda, menunjukkan kesederhanaan dan efektifitas dari kontroller yang banyak digunakan yaitu PID, dapat melakukan pengamatan terhadap sinyal digital dan analog untuk mengembangkan pemahaman tentang metode yang sedang digunakan, dan menyediakan fasilitas cocok untuk para operator dalam praktek menemukan dan menyelesaikan permasalahan. Komponen utama pada PCT-100 terdiri dari process rig dan control module. Process rig dan control module dihubungkan oleh port serial untuk melakukan proses pertukaran data. Beberapa komponen yang terdapat pada PCT-100, diantaranya:

1. Sump tank, tempat fluida proses dipompa.
2. Pompa, mensirkulasikan air keseluruh sistem. Pompa ini digerakkan oleh motor DC dan kecepatannya dapat diatur melalui kontroller terhadap referensi flow rate.
3. Flow meter bertipe turbine, mengukur flow rate air.
4. Process tank, tempat terjadinya proses utama.
5. Sensor level
6. Vent pipe

Berdasarkan datasheet, spesifikasi modul proses PCT-100 yang digunakan disajikan pada tabel di bawah (Bytronic, 2015).

Tabel 2.2 Spesifikasi Plant PCT-100

No. | Modul Proses | Spesifikasi
1 | Sump tank volume | 8 lt
2 | Process tank volume | 4.5 lt
3 | Flow rate (max.) | ~3 lt/min
4 | Control elements | 2x24VDC proportional valve, 1 finger type drain valve.
5 | Pump | 24v and 7 litres per minute open flow rate with 1.5 bar safety cut-out
6 | Safety switch | 3 bar Cracking Valve
7 | Number of LCD display | 5 x Fluid level: process tank and sump tank temperature: pressure level and flow rate
8 | Indicators | 4 x Heater on: drain valve open: diverter solenoid active and cooler active
9 | Connections | 2 x 25 way ‘D’ connectors

#### 1.2.3.2 Data Actuisition ADAM 5000L TCP


Gambar 2.2 Data Actuisition ADAM5000L/TCP

Perangkat keras ADAM 5000 TCP digunakan sebagai pengontrol/eksekutor untuk menjalankan proses. Hal ini dikarenakan perangkat keras ADAM 5000 TCP bekerja setelah diberikan masukan dari PC Human Interface Station. Perangkat keras ADAM 5000 TCP lebih banyak digunakan sebagai I/O dari proses kontrol yang dirancang. Untuk menjalankan alat ini, perintah dikirim melalui jaringan ethernet dengan komunikasi modbus.

Advantech ADAM 5000 TCP terdiri empat modul, yaitu modul 5050, modul 5024, modul 5024 dan modul 5017. Modul 5050 merupakan masukan atau keluaran digital, sedangkan modul 5024 dan modul 5017 merupakan keluaran dan masukan analog. Pada perancangan sistem kontrol proses ini, hanya menggunakan dua modul. Dua modul yang digunakan yaitu, modul ADAM 5024 yang merupakan modul keluaran analog. Modul ADAM 5024 terdiri dari empat channel untuk memberikan masukan berupa arus dan empat channel masukan berupa tegangan. Modul lain yang digunakan pada perancangan sistem kontrol proses, yaitu modul ADAM 5017 yang merupakan modul masukan analog. Pada modul ini, terdiri dari delapan channel yang digunakan untuk melihat besarnya nilai keluaran dari plant.

### 1.2.4 Kontroller PID

### 1.2.5 Jaringan syaraf tiruan (Artificial Neural Network)

Artificial Neural Network bekerja menurut prinsip kerja jaringan syaraf manusia. Dari Gambar di bawah dapat dilihat, bahwa sebuah neuron mendapatkan input dari dendrit dan memberikan output melalui akson. Informasi masuk kedalam syaraf melalui dendrit. Dendrit ini bertugas mengumpulkan informasi dan meneruskannya ke badan sel. Pada badan sel, informasi yang telah dikumpulkan diolah dengan proses tertentu dan menghasilkan sinyal output. Output dari badan sel diteruskan ke sel syaraf berikutnya melalui akson. Akson ini akan terhubung dengan dendrit sel syaraf berikutya. Sambungan akson sel syaraf satu dengan dendrit sel syaraf lainnya disebut sinapsis. Kekuatan sambungan pada sinapsis menentukan seberapa besar informasi yang diteruskan oleh sel syaraf sebelumnya dapat diterima oleh sel syaraf berikutnya, yang kemudian disebut dengan bobot.


Tiruan neuron dalam struktur Neural Network adalah sebagai elemen proses yang dapat berfungsi seperti halnya sebuah neuron. Model dari neuron pada Neural Network ini seperti pada Gambar 2.8, dimana pi merupakan input pada neuron dan wi merupakan bobot atau weight. Sinyal input pi ini akan dikalikan dengan nilai wi. Nilai output dari neuron ini dapat dirumuskan seperti pada Persamaan berikut

a=f(z)=f((∑_(i=1)^n p_i w_i )-θ)

Dimana θ merupakan nilai bias, dan f merupakan fungsi aktivasi pada neuron. Tingkat aktivasi dari neuron dapat berharga diskrit yaitu 0 dan 1, atau kontinyu yaitu antara 0 dan 1. Hal tersebut bergantung pada fungsi aktivasi yang digunakan. Ada berbagai macam fungsi aktivasi yang digunakan diantaranya Treshold function, Hard limit function, Sigmoid function, dan Linear Function. Dari macam-macam fungsi aktivasi pada neuron yang paling sering digunakan adalah sigmoid function karena dianggap lebih mendekati dari kinerja sinyal pada otak manusia.

### 1.2.6 Cascade Neuro-PID


Gambar 2.3 Kontroller cascade neuro PID (Zhang et al., 2012)

Kontroller neuro PID yang dirancang tersusun atas 3 jenis layer, yaitu satu input layer, satu output layer, dan beberapa hidden layer yang divariasikan.


Gambar 2.4 Struktur Neural Network untuk Autotune PID

Pada algoritma neural network, terdapat mekanisme feedforward dan backpropagation. Algoritma feedforward akan menghitung maju input layer menuju output layer, lalu dibandingkan nilai output dengan referensi yang digunakan. Jumlah neuron pada input layer disesuaikan dengan variable masukan layer. Persamaan berikut menyatakan keluaran input layer ke input hidden layer.

O_j^1 =x(j) (j=1,2,…,M)

M merupakan jumlah neuron input layer, dimana terdapat error (e), derivative error (de), integrator error (∫e), setpoint Ud, dan keluaran plant Qin. Persamaan berikut merupakan input ke hidden layer yang akan diaktivasi fungsi tanh sigmoid O_i^((2)) .

net_1^((2)) =∑_(j=0)^M w_(ij)^((2)) O_j^((1))

O_i^((2)) (k)=f(net_1^((2)) (k)) (i=1,2,…,Q)

f(x)=(e^x -e^(-x))/(e^x +e^(-x))

Q merupakan jumlah neuron hidden layer, f ialah fungsi aktivasi hidden layer, w_(ij) ialah bobot input layer ke hidden layer. Sementara itu dengan cara yang sama, keluaran output layer dapat dituliskan sebagai berikut.

net_1^((3)) =∑_(i=0)^Q w_(ij)^((3)) O_i^((3))

O_l^((3)) (k)=g(net_l^((3)) (k)) (l=1,2,3)

g merupakan fungsi aktivasi output layer yang nilainya non negative, sehingga digunakan fungsi aktivasi non negative sigmoid.

g(x)=(e^x)/(e^x +e^(-x))

Keluaran dari output layer merupakan nilai Kp, Ki, dan Kd seperti persamaan berikut.

O_1^((3)) (k)=Kp

O_2^((3)) (k)=Ki

O_3^((3)) (k)=Kd

Mekanisme backpropagation akan merubah nilai bobot neuron melalui nilai error atau indeks performansi. Perubahan bobot hidden layer ke output layer diberikan dengan persamaan berikut.

∆w_(li)^((3)) (k)=-η(∂E)/(∂w_(li)^((3)))+αw_(li)^((3)) (k-1)

w_(li)^((3)) (k+1)=w_(li)^((3)) (k)+∆w_(li)^((3)) (k)

∆w_(li)^((3)) (k+1)=α∆w_(li)^((3)) (k-1)+ηδ_l^((3)) O_i^((2)) (k)

δ_l^((3)) =e(k)(∂y(k))/(∂u(k))(δu(k))/(δO_i^((3)) (k))g^(') (in_l^((3)) (k))

g^(') (x)=g(x)(1-g(x))

Sementara itu dengan cara yang sama, untuk perubahan bobot input layer ke hidden layer diberikan oleh persamaan berikut.

w_(ij)^((2)) (k+1)=w_(ij)^((2)) (k)+∆w_(ij)^((2)) (k)

∆w_(ij)^((2)) (k)=α∆w_(ij)^((2)) (k-1) δ_i^((2)) O_j^((1)) (k)

δ_l^((2)) =f^(') (in_l^((2)) (k)) ∑_(l=1)^3 δ_l^((3)) w_(li)^((3)) (k)

# BAB 2 METODOLOGI

## 2.1 Metode yang digunakan

Metode yang digunakan dalam merancang controller adaptif neuro PID terbagi atas 2 tahapan, yakni eksperimen simulasi dan implementasi. Tahapan perancangan controller tersaji dalam flow diagram berikut.


Gambar 3.1 Langkah Pengerjaan

1. Studi literatur

Pengerjaan tugas akhir ini diawali dengan studi literatur yang membahas tentang kontrol adaptif, cascade, dan neural network. Sumber literatur bersumber dari textbook, manual alat, dan jurnal penelitian sebelumnya.

2. Perancangan model plant

Perancangan model diperlukan untuk mengidentifikasi respon system dari parameter plant. Perancangan ini juga memerlukan pengambilan data training melalui software PCT-100. Data yang diperoleh nantinya digunakan untuk menyusun spesifikasi simulasi neural network. Proses analisis model dan data training diperlukan untuk menyusun algoritma simulasi yang sesuai.

3. Simulasi model plant pada MATLAB

Simulasi plant dilakukan menggunakan MATLAB dan data process value yang diperoleh sebelumnya. Tuning simulasi dilakukan dengan mengambil data training plant dan melatihnya secara offline tuning. Simulasi model diharapkan memenuhi spesifikasi respon berupa error steady state yang rendah dan meminimalkan overshoot. Apabila tujuan ini sudah terpenuhi, diperlukan implementasi pada plant sebagai penerapan dari model simulasi.

4. Perancangan alat dan wiring

Tahapan ini merupakan langkah implementasi dari model simulasi yang berhasil dibangun. Perancangan alat meliputi tahap penyiapan alat, wiring instrument berdasarkan manual, serta konfigurasi software (Python, PyCharm, dan ADAM Apax .Net) sebagai computer controller.

5. Implementasi program pada PCT

Setelah alat dan wiring sudah dipasang dan dapat dieksekusi oleh computer, implementasi dilanjutkan dengan mengeksekusi program kontrol dalam kode Python. Program berjalan secara realtime untuk menguji performansi dengan online tuning.

6. Pengambilan data dan evaluasi

Untuk melihat performansi pengujian implementasi dengan online tuning, respon sistem berupa error steady state dan overshoot perlu dianalisis sebagai bahan evaluasi. Apabila hasil kurang sesuai, dilakukan perbaikan pada kode program hingga mendapat respon yang sesuai dengan tujuan implementasi.

7. Penyusunan buku tugas akhir

Tahapan terakhir, diperlukan penyusunan buku tugas akhir untuk mendokumentasi penelitian yang dilakukan dan luaran untuk publikasi.

Perancangan kontroller PID-NN tersusun atas kontroller PID sebagai kontroller utama dan neural network sebagai kontroller cerdas yang mampu melakukan autotuning parameter PID. Kontroller ini dapat didesain melalui langkah berikut.

1. Menentukan algoritma learning yang akan dipakai pada neural network. Pada penelitian ini digunakan backpropagation.
2. Menentukan struktur neural network, yakni jumlah layer dan neuron tiap layer.
3. Melakukan pembobotan pada input, hidden, dan output layer.
4. Menentukan learning rate.

## 2.2 Bahan dan peralatan yang digunakan

Perngerjaan tugas akhir ini memerlukan bahan dan peralatan sebagai berikut.

1. Modul plant PCT-100
2. Data Actuisition ADAM5000L
3. Laptop OS Windows 10
4. Python 3.8 dan PyCharm IDE
5. MATLAB dan SIMULINK v2021b

## 2.3 Urutan pelaksanaan penelitian

Penjadwalan pengerjaan tugas akhir disusun agar proses pengerjaan berlangsung pada waktu yang sesuai dan selesai tepat waktu. Penjadwalan ini ditentukan berdasar perkiraan bobot tiap kegiatan pengerjaan. Urutan pelaksanaan disajikan pada tabel di bawah.

Tabel 3.1 Timeline Pengerjaan Tugas Akhir

No. | Kegiatan | Minggu ke-
| | 1 | 2 | 3 | 4 | 5 | 6 | 7 | 8 | 9 | 10 | 11 | 12 | 13 | 14 | 15 | 16
1 | Studi literatur
2 | Perancangan model plant
3 | Simulasi model pada MATLAB
4 | Perancangan alat dan wiring
5 | Implementasi program pada PCT-100
6 | Pengambilan data
7 | Analisis data pengujian
8 | Penyusunan buku TA

# DAFTAR PUSTAKA

Bytronic. (2015). Process Control Technology PCT-100 Datasheet. http://www.bytronic.net/wp-content/uploads/2015/04/PCT100-PL0214.pdf

Ghufron, M. Z. (2016). DESAIN DAN IMPLEMENTASI KONTROLER SELF-TUNING PID DENGAN PENDEKATAN INTERAKSI ADAPTIF PADA SISTEM PENGATURAN LEVEL.

Padhan, D. G., & Majhi, S. (2012). Modified Smith predictor based cascade control of unstable time delay processes. ISA Transactions, 51(1), 95–104. https://doi.org/10.1016/J.ISATRA.2011.08.002

Patel, R., & Kumar, V. (2015). Multilayer Neuro PID Controller based on Back Propagation Algorithm. Procedia Computer Science, 54, 207–214. https://doi.org/10.1016/j.procs.2015.06.023

Raharjo, R. D. (2014). DESAIN DAN IMPLEMENTASI KONTROLER PID GAIN SCHEDULING UNTUK SISTEM PENGATURAN PROSES LEVEL PADA PROCESS CONTROL TECHNOLOGY - 100. Institut Teknologi Sepuluh Nopember.

Zhang, J., Zhang, F., Ren, M., Hou, G., & Fang, F. (2012). Cascade control of superheated steam temperature with neuro-PID controller. ISA Transactions, 51(6), 778–785. https://doi.org/10.1016/j.isatra.2012.06.008

# LAMPIRAN

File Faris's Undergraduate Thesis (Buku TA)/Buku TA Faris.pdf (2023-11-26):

### TUGAS AKHIR – EE184801

PERANCANGAN | KONTROLER | TERTANAM

## MENGGUNAKAN DIRECT NEURAL NETWORK UNTUK PENGATURAN LEVEL TANGKI PCT-100

### MUHAMMAD FARIS ZUHAIRI

### NRP 07111940000164

### Dosen Pembimbing

Eka Iskandar, S.T., M.T.

### NIP 198005282008121001

Dr. Trihastuti Agustinah, S.T., M.T.

### NIP 196808121994032001

### Program Studi Teknik Sistem Pengaturan

Departemen Teknik Elektro

Fakultas Teknologi Elektro dan Informatika Cerdas

Institut Teknologi Sepuluh Nopember

Surabaya

2023

### TUGAS AKHIR – EE184801

PERANCANGAN | KONTROLER | TERTANAM

## MENGGUNAKAN DIRECT NEURAL NETWORK UNTUK PENGATURAN LEVEL TANGKI PCT-100

### MUHAMMAD FARIS ZUHAIRI

### NRP 07111940000164

### Dosen Pembimbing

Eka Iskandar, S.T., M.T.

### NIP 198005282008121001

Dr. Trihastuti Agustinah, S.T., M.T.

### NIP 196808121994032001

### Program Studi Teknik Sistem Pengaturan

Departemen Teknik Elektro

Fakultas Teknologi Elektro dan Informatika Cerdas

Institut Teknologi Sepuluh Nopember

Surabaya

2023

### FINAL PROJECT – EE184801

## EMBEDDED CONTROLLER DESIGN USING DIRECT NEURAL NETWORK FOR LEVEL CONTROL IN PCT-100 TANK

### MUHAMMAD FARIS ZUHAIRI

### NRP 07111940000164

### Advisor

Eka Iskandar, S.T., M.T.

### NIP 198005282008121001

Dr. Trihastuti Agustinah, S.T., M.T.

### NIP 196808121994032001

### Study Program Control System Engineering

Department of Electrical Engineering

Faculty of Intelligent Electrical and Informatics Technology

Institut Teknologi Sepuluh Nopember

Surabaya

2023

i

LEMBAR PENGESAHAN

PERANCANGAN KONTROLER TERTANAM MENGGUNAKAN DIRECT NEURAL NETWORK UNTUK PENGATURAN LEVEL TANGKI PCT-100

TUGAS AKHIR

Diajukan untuk memenuhi salah satu syarat

memperoleh gelar Sarjana Teknik pada

Program Studi S-1 Teknik Sistem Pengaturan

Departemen Teknik Elektro

Fakultas Teknologi Elektro dan Informatika Cerdas

Institut Teknologi Sepuluh Nopember

Oleh : MUHAMMAD FARIS ZUHAIRI

NRP. 07111940000164

Disetujui oleh Tim Penguji Tugas Akhir :

1. Eka Iskandar, S.T., M.T. | Pembimbing
2. Dr. Trihastuti Agustinah, S.T., M.T. | Ko-pembimbing
3. Yurid Eka Nugraha, S.T, M.Eng, Ph.D. | Penguji
4. Ir. Ali Fatoni, M.T. | Penguji
5. Dr. Ir. Ari Santoso, DEA. | Penguji

SURABAYA

Juli, 2023

ii

PERNYATAAN ORISINALITAS

Yang bertanda tangan di bawah ini:

Nama mahasiswa / NRP | : Muhammad Faris Zuhairi
Program studi | : Teknik Sistem Pengaturan
Dosen Pembimbing / NIP | : Eka Iskandar, S.T., M.T. / 198005282008121001
| Dr. Trihastuti Agustinah, S.T., M.T. /
| 196808121994032001

dengan ini menyatakan bahwa Tugas Akhir dengan judul “Perancangan Kontroler Tertanam Menggunakan Direct Neural Network untuk Pengaturan Level Tangki PCT-100” adalah hasil karya sendiri, bersifat orisinal, dan ditulis dengan mengikuti kaidah penulisan ilmiah.

Bilamana di kemudian hari ditemukan ketidaksesuaian dengan pernyataan ini, maka saya bersedia menerima sanksi sesuai dengan ketentuan yang berlaku di Institut Teknologi Sepuluh Nopember.

Surabaya, 8 Juli 2023

Mengetahui,
Dosen Pembimbing 1 | Dosen Pembimbing 2
Eka Iskandar, S.T., M.T. | Dr. Trihastuti Agustinah, S.T., M.T.
NIP. 198005282008121001 | NRP. 196808121994032001

Mahasiswa

Muhammad Faris Zuhairi
NRP. 07111940000164

iii

ABSTRAK

PERANCANGAN KONTROLER TERTANAM MENGGUNAKAN DIRECT NEURAL NETWORK UNTUK PENGATURAN LEVEL TANGKI PCT-100

Nama Mahasiswa / NRP | : Muhammad Faris Zuhairi/07111940000164
Departemen | : Teknik Elektro FTEIC - ITS
Dosen Pembimbing | : Eka Iskandar, S.T., M.T.
| Dr. Trihastuti Agustinah, S.T., M.T.

Abstrak

Level tangki PCT-100 memiliki karakteristik nonlinear akibat keluaran air drain valve. Kemampuan self learning kontroler dibutuhkan untuk mengatasi perubahan beban. Kontroller direct neural network dapat mengendalikan level dengan mengambil input error dan secara langsung mengirim output sinyal kontrol. Namun algoritma cerdas kontroler membutuhkan pemilihan nilai learning rate yang tepat agar medapat spesifikasi respon yang diinginkan. Spesifikasi ini berupa overshoot level kurang dari 10% dan settling time 5% kurang dari 200 detik saat pembebanan valve dan tracking set point. Selain itu, aktuator flow control valve membutuhkan daya yang besar sehingga harus dibuat kontroler tertanam agar sinyal kontrol langsung melakukan penguatan daya untuk membuka valve. Rangkaian conditioning yang dibuat memberikan hasil linear dengan kesalahan pengukuran maksimal sebesar 121.6mV untuk pembacaan sensor dan 489mV untuk tegangan kontrol. Kontroler neural network dengan learning rate sebesar 10 memiliki hasil terbaik dari sampel uji learning rate konstan, mampu beradaptasi dengan beban motor drain valve dengan overshoot 12% dan settling time 161.7 detik. Adaptasi learning rate melalui parameter alpha juga dapat mengatasi perubahan beban drain terhadap error proses dengan model terbaik saat alpha=0.1, dimana overshoot dan settling time masing-masing sebesar 3.8% dan 111.5 detik untuk simulasi serta 3.43% dan 127.2 detik untuk implementasi. Model neural network yang dibuat mampu melakukan tracking terhadap perubahan set point naik dan turun dengan overshoot dan undershoot yang semakin kecil untuk step setpoint selanjutnya.

Kata kunci: PCT-100, Neural Network, Learning Rate, Sistem Tertanam

iv

ABSTRACT

EMBEDDED CONTROLLER DESIGN USING DIRECT NEURAL NETWORK FOR LEVEL CONTROL IN PCT-100 TANK

Student Name / NRP | : Muhammad Faris Zuhairi/07111940000164
Department | : Teknik Elektro FTEIC - ITS
Advisor | : Eka Iskandar, S.T., M.T.
| Dr. Trihastuti Agustinah, S.T., M.T.

Abstract

PCT-100 tank level having nonlinear characteristic, caused by valve water outflow. Controller’s learning capabilities is needed to reduce load changes. Direct neural networks controller capable to control process level by taking error as input and directly sending its output as control signal. However, controller’s intelligent algorithm requires selecting learning rate correctly to get desired response specification, that is overshoot less than 10% and settling time 5% less than 200s when load and setpoint changes. In addition, flow motor valve having high power electronics to be actuated. Embedded controller can be implemented so that control signal amplify motor valve voltage. The conditioning circuit that’s been created provides linear results with a maximum measurement error of 121.6mV for sensor readings and 489mV for controling voltage. The neural network controller with a learning rate 10 achieves the best results among the constant learning rate test samples, capable of adapting water outflow load with 12% overshoot and 161.7 seconds settling time. Adapting the learning rate through the alpha parameter can overcome changes in the drain load affecting the process error with alpha=0.1 as the best model, resulting 3.8% overshoot and 111.5 seconds settling time for simulation, and 3.43% and 127.2 seconds for implementation, respectively. The neural network model is able to track changes in the set point, both increasing and decreasing, with diminishing overshoot and undershoot for subsequent setpoint steps.

Keywords: PCT-100, Neural Network, Learning Rate, Embedded System.

v

KATA PENGANTAR

Puji syukur penulis panjatkan kepada Allah S.W.T yang telah memberikan rahmat dan hidayah-Nya sehingga penulis dapat menyelesaikan tugas akhir ini dengan baik dan tepat waktu. Kegiatan tugas akhir ini merupakan salah satu syarat untuk menyelesaikan program studi Sarjana di Departemen Teknik Elektro Institut Teknologi Sepuluh Nopember.

Penulis sadar bahwa tugas akhir ini tidak akan terwujud tanpa dukungan dan bantuan dari berbagai pihak. Oleh sebab itu, penulis menyampaikan rasa terima kasih kepada pihak-pihak yang turut membantu penulis dalam menyelesaikan tugas akhir ini, yaitu kepada:

1. Kedua orang tua penulis yang telah memberikan doa dan dukungan kepada penulis selama proses perkuliahan.
2. Bapak Eka Iskandar, S.T., M.T. dan Ibu Dr. Trihastuti Agustinah, S.T., M.T. sebagai dosen pembimbing yang telah memberikan bimbingan dan arahan selama pengerjaan tugas akhir ini.
3. Bapak dan Ibu dosen Departemen Teknik Elektro FTEIC ITS, khususnya bidang studi Teknik Sistem Pengaturan.
4. Hakhi, Usama, dan Reno yang ikut membantu pengerjaan prototype dan permodelan PCT-100.
5. Teman-teman e59 dan e60 khususnya Asisten Laboratorium Kontrol dan Otomasi yang membantu dalam diskusi dan dukungan untuk penyelesaian tugas akhir ini.

Besar harapan penulis agar laporan tugas akhir dengan judul Perancangan Kontroler Tertanam Menggunakan Direct Neural Network untuk Pengaturan Level Tangki PCT-100 ini dapat berguna serta memberikan wawasan lebih bagi pembaca. Penulis juga menyadari masih ada kekurangan dan kesalahan dalam tugas akhir ini, mengingat keterbatasan pengetahuan dan pengalaman penulis. Oleh karena itu, penulis memohon maaf atas kesalahan yang mungkin ditemukan di dalamnya. Penulis juga mengharapkan saran dan kritik agar penulis dapat berkembang lagi menjadi lebih baik.

Surabaya, 8 Juli 2023

Penulis

vi

DAFTAR ISI

LEMBAR PENGESAHAN | i
PERNYATAAN ORISINALITAS | ii
ABSTRAK | iii
ABSTRACT | iv
KATA PENGANTAR | v
DAFTAR ISI | vi
DAFTAR GAMBAR | viii
DAFTAR TABEL | x
DAFTAR SIMBOL | xi
BAB 1 | PENDAHULUAN | 12
1.1 | Latar Belakang | 12
1.2 | Rumusan Masalah | 12
1.3 | Batasan Masalah | 13
1.4 | Tujuan | 13
1.5 | Manfaat | 13
BAB 2 | TINJAUAN PUSTAKA | 14
2.1 | Hasil Penelitian Terdahulu | 14
2.2 | Dasar Teori | 14
2.2.1 | PCT-100 | 14
2.2.2 | Permodelan Plant | 16
2.2.3 | Direct Control Neural Network | 22
BAB 3 | METODOLOGI | 26
3.1 | Metode yang digunakan | 26
3.2 | Bahan dan peralatan yang digunakan | 27
3.3 | Urutan pelaksanaan penelitian | 27
3.3.1 | Permodelan Plant | 27
3.3.2 | Perancangan Sistem Tertanam | 36
3.3.3 | Perancangan Kontroler | 39
BAB 4 | HASIL DAN PEMBAHASAN | 44
4.1 | Pengujian Rangkaian Analog Input | 44
4.2 | Pengujian Rangkaian Analog Output | 45
4.3 | Pengujian pada Kondisi Berbeban Tanpa Kontroler | 47

vii

4.4 | Pengujian pada Kondisi Berbeban dengan Learning Rate Konstan | 47
4.5 | Pengujian pada Kondisi Berbeban dengan Adaptasi Learning Rate | 49
4.6 | Pengujian pada Kondisi Berbeban terhadap Tracking Set Point | 52
4.7 | Implementasi Berbeban pada Kontroler Tertanam | 55
BAB 5 | KESIMPULAN DAN SARAN | 61
5.1 | Kesimpulan | 61
5.2 | Saran | 61
DAFTAR PUSTAKA | 62
LAMPIRAN | 63
BIODATA PENULIS | 69

viii

DAFTAR GAMBAR

Gambar 2.1 Process Rig PCT-100 | 15
Gambar 2.2 Control Module PCT-100 | 16
Gambar 2.3 STM32F407 Discovery Board | 16
Gambar 2.4 Arsitektur Hardware PCT-100 | 17
Gambar 2.5 Penempatan Floating Ball pada Tangki Proses | 18
Gambar 2.6 Bagan Sistem Tangki Tunggal Tanpa Flow Masuk | 19
Gambar 2.7 Sistem Tangki Tunggal Dengan Tambahan Flow Masuk | 20
Gambar 2.8 Blok Diagram Matematis Sistem Level Tangki SISO (Prusty, 2012) | 21
Gambar 2.9 Struktur Neural Network (Haykin, 2009) | 22
Gambar 2.10 Closed Loop Diagram dengan Direct Neural Network (Ponce et al., 2004)22
Gambar 2.11 Struktur Kontroler Neural Network (Ponce et al., 2004) | 23
Gambar 3.1 Flowchart Metodologi Penelitian | 26
Gambar 3.2 Respon tegangan Level Sensor terhadap Level Air | 27
Gambar 3.3 Respon Tegangan Flow terhadap Variasi Tegangan Pompa | 28
Gambar 3.4 Respon Level Air terhadap Variasi Tegangan Pompa | 29
Gambar 3.5 Respon tegangan flow meter VFT terhadap laju level tangki (∆ℎ/∆t) .........30
Gambar 3.6 Respon Pembacaan Flow Meter Setelah Substitusi Nilai Gain mFT | 31
Gambar 3.7 Perbandingan fungsi alih flow valve dan data sebenarnya | 32
Gambar 3.8 Respon Level untuk Identifikasi Ao Motor Valve | 33
Gambar 3.9 Respon Flow untuk Identifikasi Ao Motor Valve | 33
Gambar 3.10 Respon Level untuk Identifikasi Ao Manual Valve | 34
Gambar 3.11 Respon Flow untuk Identifikasi Ao Motor Valve | 34
Gambar 3.12 Respon Level untuk Identifikasi Ao Kedua Valve | 35
Gambar 3.13 Respon Flow untuk Identifikasi Ao Kedua Valve | 35
Gambar 3.14 Prototype yang telah Dirancang | 37
Gambar 3.15 Modul Power Supply, Mikrokontroler, dan USB-TTL | 37
Gambar 3.16 Rangkaian Penurun Tegangan ADC dan MicroSD Logger | 38
Gambar 3.17 Rangkaian Analog Output | 39
Gambar 3.18 Diagram Blok Sistem | 40
Gambar 3.19 Struktur Kontroler Direct Neural Network | 40
Gambar 3.20 Kurva Pembebanan Drain Valve | 42
Gambar 3.21 Kurva Uji Tracking Set Point Level | 42
Gambar 4.1 Hasil Pengukuran AI Channel 0 STM32 terhadap AO USB4716 (0-10V)...44 Gambar 4.2 Hasil Pengukuran AI Channel 1 STM32 terhadap AO USB4716 (0-10V)...44
Gambar 4.3 Rangkaian Voltage Divider AO STM32 | 45
Gambar 4.4 Pengukuran AI USB4716 terhadap AO Channel 0 STM32 (0-22V) | 46
Gambar 4.5 Pengukuran AI USB4716 terhadap AO Channel 0 STM32 (0-10V) | 46
Gambar 4.6 Respon Level Tanpa Kontroler terhadap Setpoint Konstan | 47
Gambar 4.7 Respon Level Tanpa Kontroler terhadap Perubahan Setpoint | 47
Gambar 4.8 Respon Level Tangki saat Pembebanan Learning Rate Konstan | 48
Gambar 4.9 Perubahan Sinyal Kontrol saat Pembebanan Learning Rate Konstan | 49
Gambar 4.10 Respon Level Tangki saat Pembebanan dengan Adaptasi Learning Rate ...50

ix
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

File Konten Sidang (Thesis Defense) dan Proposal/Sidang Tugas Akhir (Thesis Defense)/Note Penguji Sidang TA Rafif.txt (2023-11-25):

1. delay di input HP ke plant brp? ada rumus TF: e^-ts (time delay system untuk MQTT)
2. disuruh inputkan pid n fuzzy dr HP. 
3. model tidak dipermasalahkan. jgn cari monitoring aja di HP tapi disuruh kontrolnya via HP
4. metode kontrol samsek ditanyakan.
5. kenapa ambil level? jawab via sistem
6.

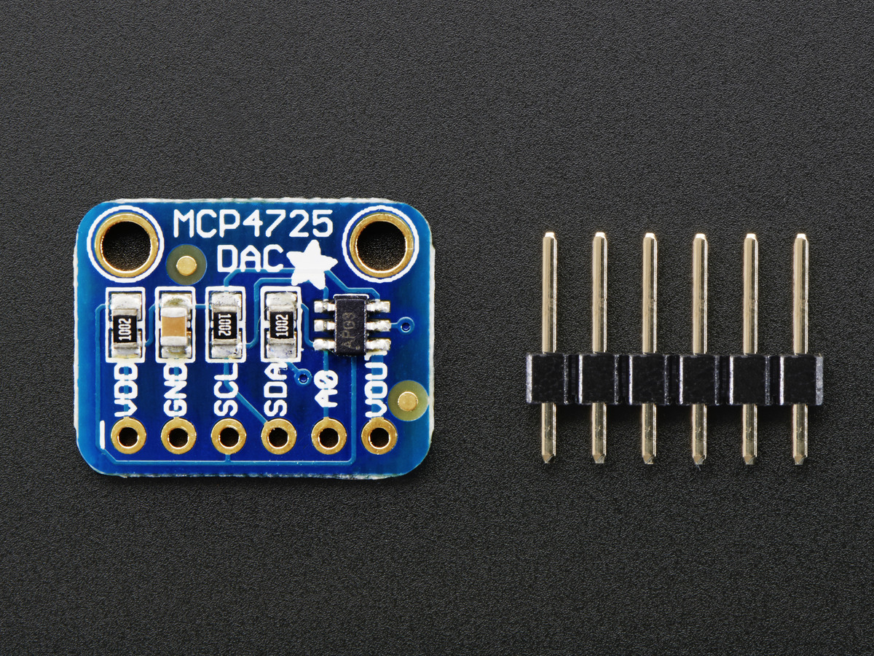
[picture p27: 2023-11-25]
Embedded System Kit PCB & Acrylic Box/Schematic PCB/Adafruit-MCP4725-PCB-master/assets/image.jpg

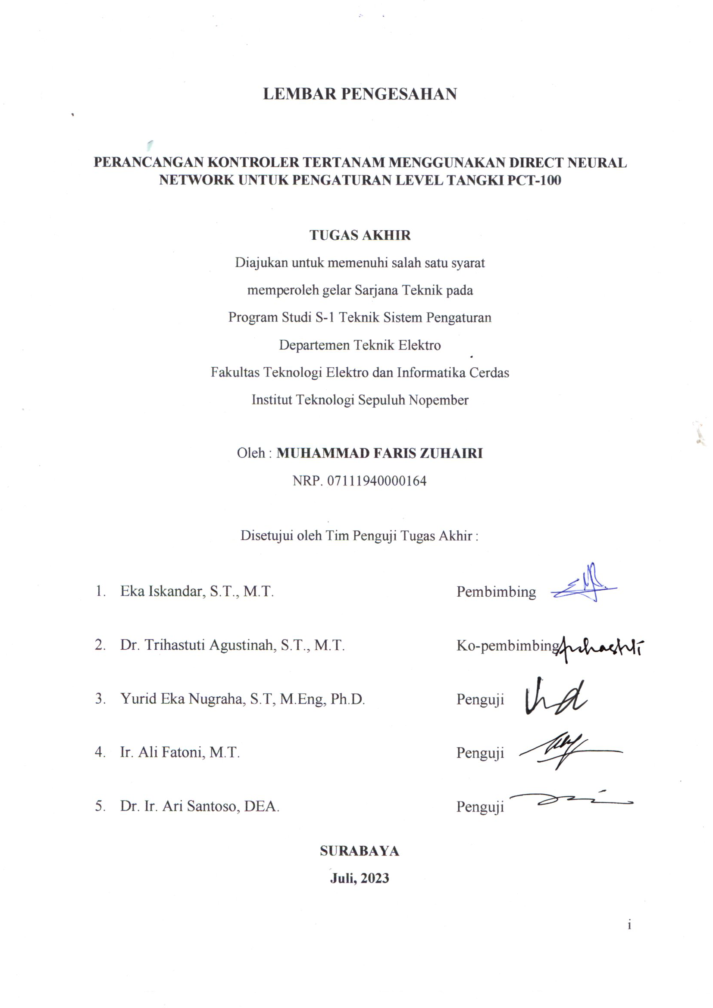
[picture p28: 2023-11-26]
Faris's Undergraduate Thesis (Buku TA)/Lembar Pengesahan.jpg

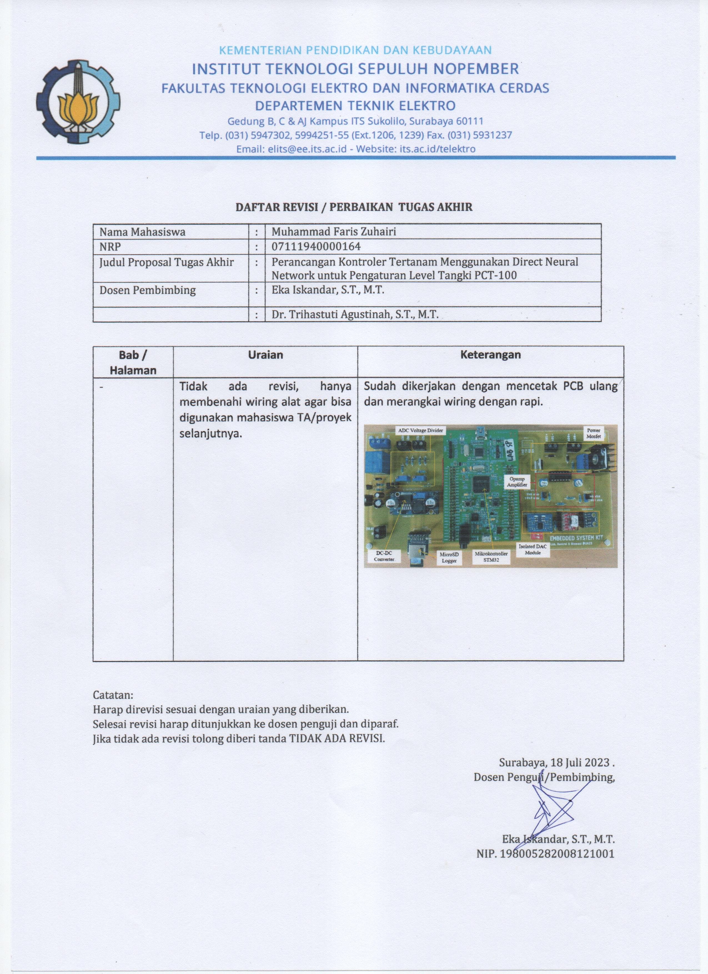
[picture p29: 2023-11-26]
Faris's Undergraduate Thesis (Buku TA)/POMITS & TA/Lembar Revisi_P.Eka.jpg

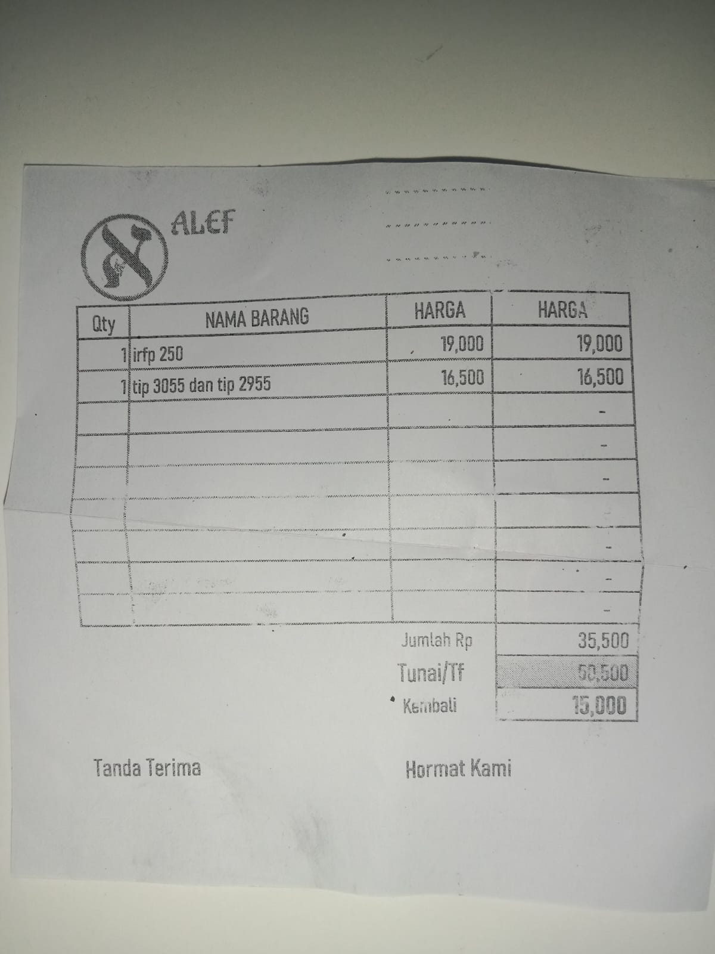
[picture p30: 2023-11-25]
Receipt & Buying Report/Faris/Alef MOSFET dan TIP.jpg

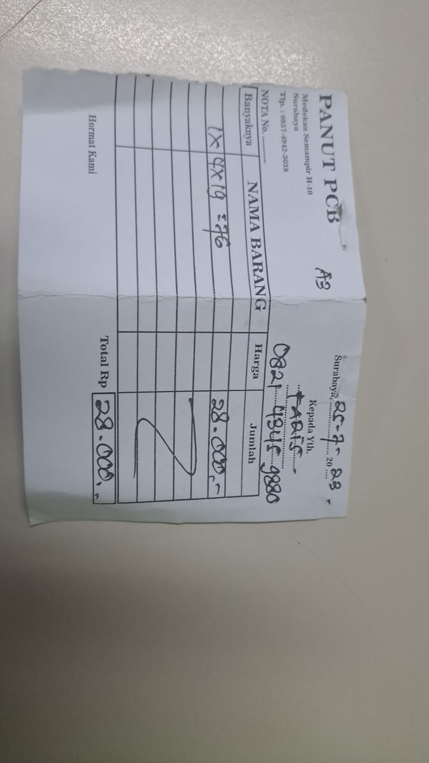
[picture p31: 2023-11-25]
Receipt & Buying Report/Haki/Pak Panut Modul Terminal.jpg

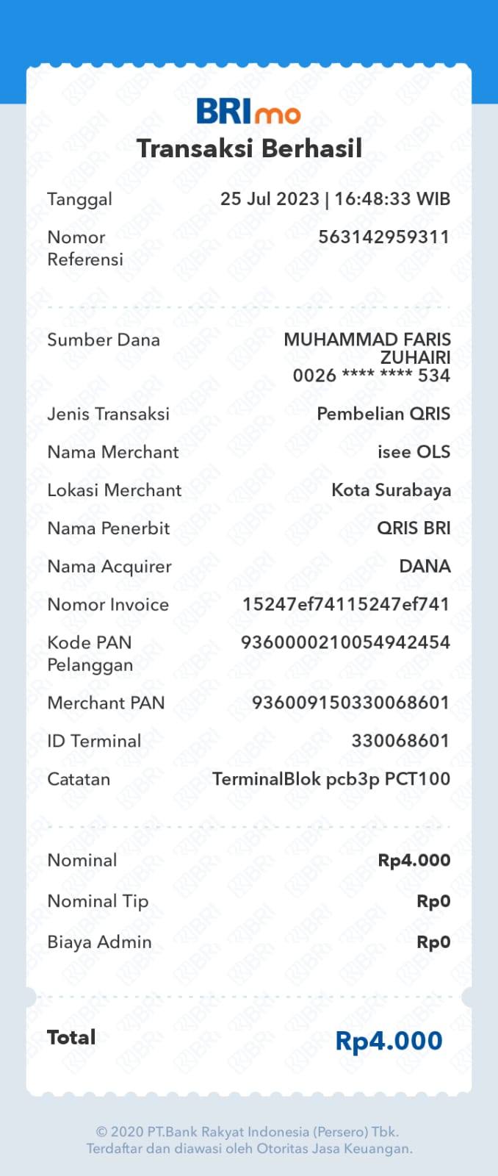
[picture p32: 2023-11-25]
Receipt & Buying Report/Faris/Isee QRIS Terminal Block 3p PCB.jpg

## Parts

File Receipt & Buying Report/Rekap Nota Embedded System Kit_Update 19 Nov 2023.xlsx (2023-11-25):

 | Rekap Nota untuk Tugas Akhir PCT-100
 | Embedded System Kit
 | Update 19/11/2023
 | Nama Periset:
 | 1. Muhammad Faris Zuhairi (07111940000164, TSP 2019)
 | 2. Hakhi Gya Yektianto (07111940000022, TSP 2019)
 | 3. Reno Darin Khalifah Panarung (07111940000156, TSP 2019) |  |  |  |  |  | Rincian Reimburse untuk Tiap Periset:
 | 4. Muhammad Lukmanul Hakim (5022201237, TSP 2020) |  |  |  |  |  | Alokasi dana dari Pak Eka Iskandar: Rp1.000.000
 |  |  | TOTAL (Rp) | 1000000
No. | Pembeli | Toko | Part | Jumlah | Tanggal Beli |  | Nama | Nominal | Jumlah Nota
1 | Faris | Akhishop | MCP4725 | 50000 | 2023-04-13 | 1 | Faris | 819700 | 24
2 | Faris | Sakinah | MicroSD 4GB | 55000 | 2023-05-03 | 2 | Haki | 114300 | 3
3 | Faris | Pak Panut | PCB Modul Kontrol | 90000 | 2023-07-14 | 3 | Reno | 20000 | 1
4 | Faris | Isee | LM2596 DCDC Conv. | 12000 | 2023-05-10 |  | TOTAL PCT: | 954000 | 28
5 | Faris | Alef | Mosfer IRFP dan TIP | 35500 | 2023-04-17
6 | Faris | Isee | GY4725 dan KF2510 | 45000 | 2023-05-24 |  | Sisa: | 46000
7 | Faris | Isee | LM7806 dan Relay Songle | 10000 | 2023-06-07 |  |  |  |  | Nominal | Jumlah Nota
8 | Faris | Akhishop | MCP4725 | 50000 | 2023-04-08 | 4 | Sisa ini untuk riset TA Motor Hakim: |  |  | 46000 | 1
9 | Faris | Isee | VR, KF2510, IRF, Konektor | 45000 | 2023-04-12
10 | Faris | Isee, QRIS | Konektor 7.62, DC 12V, KF2510 | 29500 | 2023-07-21
11 | Faris | Eltech | DB25 | 5500 | 2023-07-24
12 | Faris | Berkat | Molex, dioda, kapasitor, header | 29200 | 2023-07-15
13 | Faris | Berkat | DIP Switch | 5000 | 2023-07-12
14 | Faris | Berkat | LM7812 | 3000 | 2023-07-10
15 | Haki | Berkat | PCB Modul Terminal | 28000 | 2023-07-25
16 | Faris | Tokped Palta | ADUM1250 | 91700 | 2023-04-14
17 | Faris | Tokped Mulsanne | Soket IC, Header, Jumper | 41300 | 2023-07-14
18 | Faris | Isee, QRIS BRIMO | Terminal Block 3p PCB Hijau Big | 4000 | 2023-07-25
19 | Haki | Tokped | pipa akrilik | 26300 | 2023-07-03
20 | Haki |  | Dobel drat 2, konektor Y, sealtape | 60000
21 | Faris | Berkat | Opto 4N25, IRFZ44, TIP32, BC140 | 36000 | 2023-03-31
22 | Faris | TB. Fania PPS | Selang 5/8', Klem 3/4' | 19000 | 2023-03-27
23 | Faris | Isee | 2 PCB Single Layer dot matrix | 24000 | 2022-11-21
24 | Reno | Toeng Market | Box plastik lion star (tanpa nota) | 20000 | 2023-08-30
25 | Faris | Akhishop | MicroSD Module | 8000 | 2023-07-15
26 | Faris | HAP Laser Cut Gebang | Cetak akrilik bening 3mm | 80000 | 2023-08-10
27 | Faris | Bayu Laser Gebang Putih | Engsel akrilik 3cm | 16000 | 2023-08-10
28 | Faris | SDA Global Raden Saleh | Nut dan Nylon Tube | 35000 | 2023-08-24
29 | Hakim | Mouser Electronics | Uang sisa PCT untuk beli komponen TA Hakim | 46000 | 2023-09-18
 | Nota berikut ialah pembelian untuk TA Hakim (TSP 2020)
 | Sisa uang Rp46ribu dialokasikan untuk pembiayaan riset Motor Induksi Hakim, nominal yang lain dari sisa ini dapat diabaikan.

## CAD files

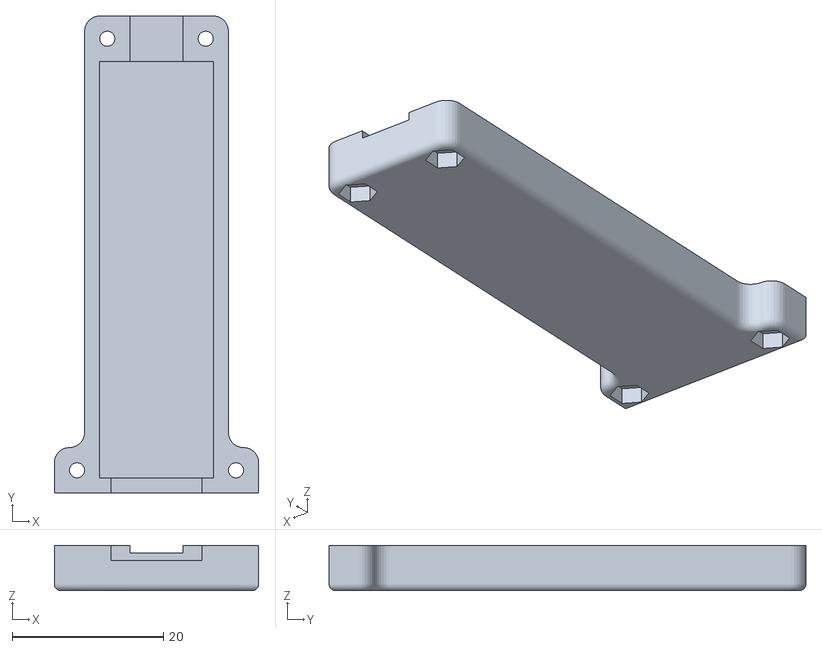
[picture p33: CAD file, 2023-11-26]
Embedded System Kit PCB & Acrylic Box/3D Akrilik/Case USB TTL 3D Print/Case Bawah.stl
27.0 x 63.0 x 6.00

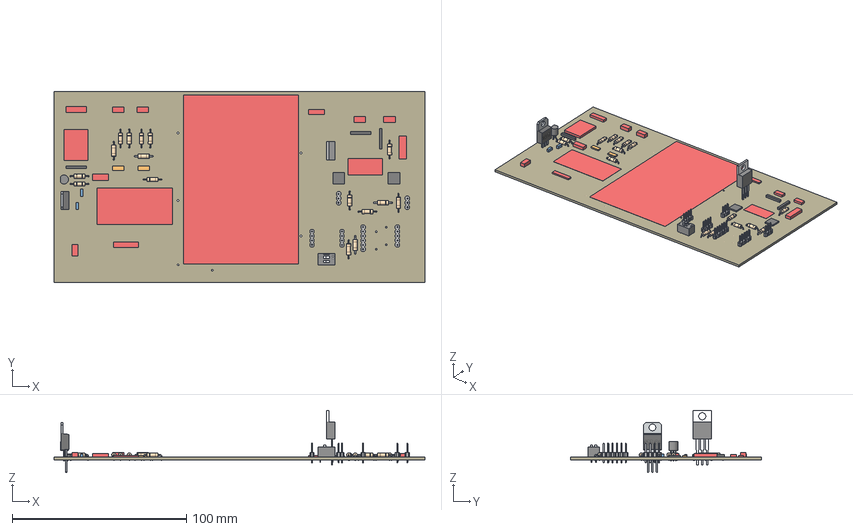
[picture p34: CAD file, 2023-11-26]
Embedded System Kit PCB & Acrylic Box/3D Akrilik/Modul PCB.step
212.7 x 109.5 x 35.8 mm
Board
STM32F407VG
1k x 16
1N4004 x 3
IRF540
IRFP250
W237-132 x 2
1X03 x 2
5k6 x 2
DC-DC-STEP-DOWN-LM2596
W237-102 x 3
G5L
BC547
W237-103
PC817
1k_1 x 2
7812TV
10uF x 2
1X05
1X06
LM324N
1X04 x 2
DS-02

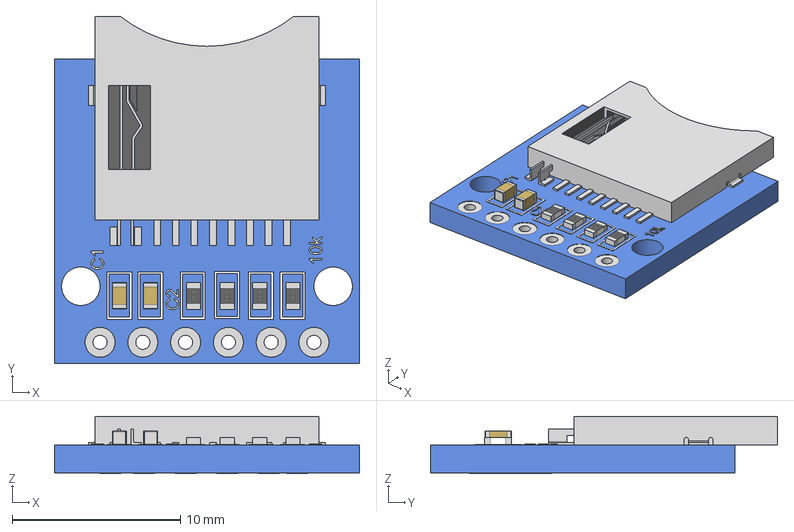
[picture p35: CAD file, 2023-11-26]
Embedded System Kit PCB & Acrylic Box/3D Akrilik/sd-card-reader-4.snapshot.4/MicroSD Card Module kecil.stp
18.1 x 20.6 x 3.40 mm
Micro SD Module - 1
MicroSD
0603 Capacitor x 2
0603 Resistor x 4

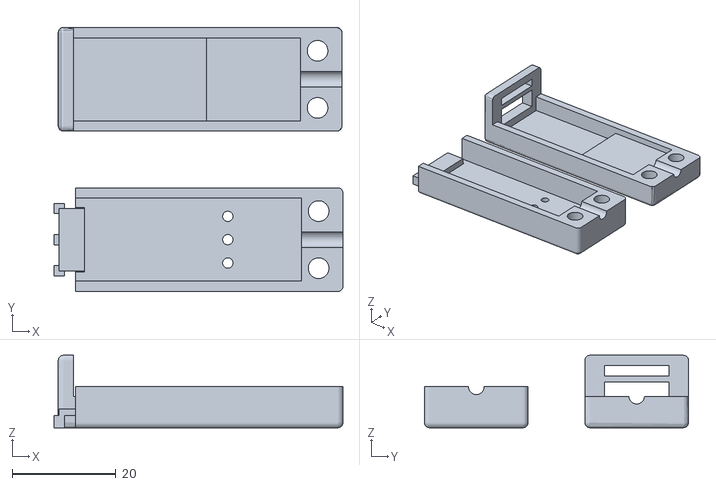
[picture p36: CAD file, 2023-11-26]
Embedded System Kit PCB & Acrylic Box/3D Akrilik/Case USB TTL 3D Print/CP2102 FTDI Case.stl
55.7 x 50.9 x 14.0

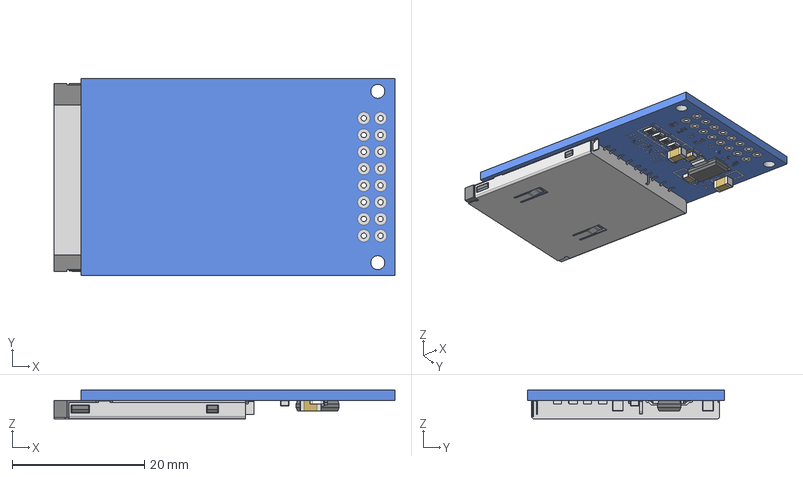
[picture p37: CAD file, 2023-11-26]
Embedded System Kit PCB & Acrylic Box/3D Akrilik/sd-card-reader-4.snapshot.4/SD Card Module - 1.stp
51.6 x 29.8 x 4.37 mm
10067847-001RLF
Board
0805 Resistor x 4
SOT223-3
1206 Capacitor x 2
0805 Capacitor x 2

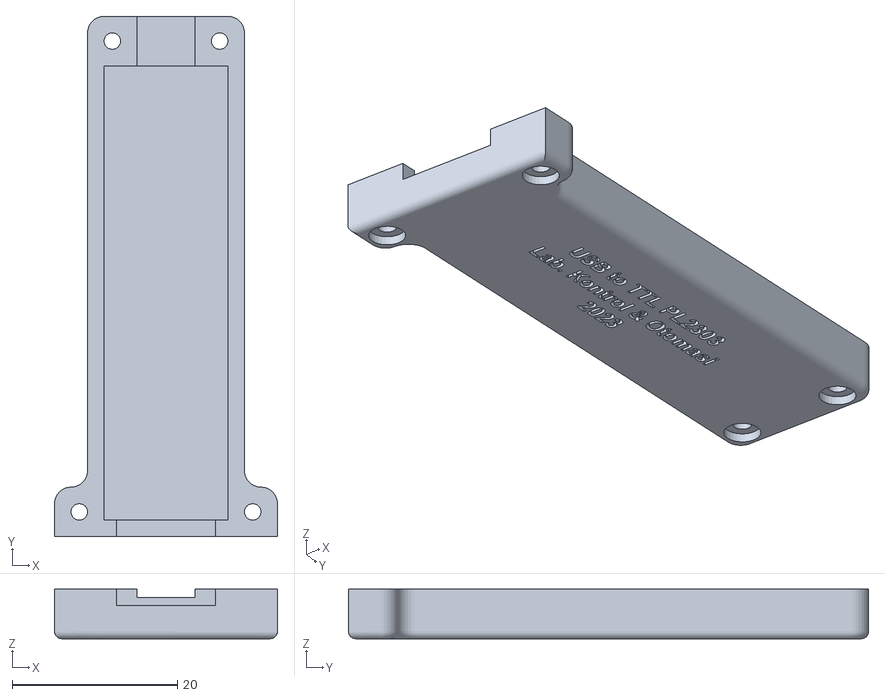
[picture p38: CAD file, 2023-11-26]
Embedded System Kit PCB & Acrylic Box/3D Akrilik/Case USB TTL 3D Print/Case Atas.stl
27.0 x 63.0 x 6.00

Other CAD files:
Embedded System Kit PCB & Acrylic Box/3D Akrilik/Kirim Cetak A2.dwg
Embedded System Kit PCB & Acrylic Box/3D Akrilik/Kirim Cetak.dwg
Embedded System Kit PCB & Acrylic Box/3D Akrilik/OldVersions/Kirim Cetak A2.0001.dwg
Embedded System Kit PCB & Acrylic Box/3D Akrilik/Alas Bawah.ipt
Embedded System Kit PCB & Acrylic Box/3D Akrilik/Atas Pintu.ipt
Embedded System Kit PCB & Acrylic Box/3D Akrilik/Atas Terminal.ipt
Embedded System Kit PCB & Acrylic Box/3D Akrilik/Belakang.ipt
Embedded System Kit PCB & Acrylic Box/3D Akrilik/CP2102 FTDI Case.ipt
Embedded System Kit PCB & Acrylic Box/3D Akrilik/Case USB TTL 3D Print/Assembly Case USB TTL.iam
Embedded System Kit PCB & Acrylic Box/3D Akrilik/Case USB TTL 3D Print/Case Atas.ipt
Embedded System Kit PCB & Acrylic Box/3D Akrilik/Case USB TTL 3D Print/Case Bawah.ipt
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

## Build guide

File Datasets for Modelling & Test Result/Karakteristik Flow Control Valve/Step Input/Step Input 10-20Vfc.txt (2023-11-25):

k, timestamp, MV_volt_FCValve, MV_volt_pompa, bit_flow, bit_level, bit_PA2
1, 107, 0.000000, 0.000000, 20, 0, 284
2, 161, 0.000000, 0.000000, 22, 0, 280
3, 215, 0.000000, 0.000000, 16, 0, 284
4, 269, 0.000000, 0.000000, 12, 0, 282
5, 323, 0.000000, 0.000000, 18, 0, 280
6, 376, 0.000000, 0.000000, 12, 0, 277
7, 430, 0.000000, 0.000000, 13, 0, 286
8, 484, 0.000000, 0.000000, 10, 0, 280
9, 538, 0.000000, 0.000000, 16, 0, 283
10, 593, 0.000000, 0.000000, 10, 0, 286
11, 647, 0.000000, 0.000000, 20, 0, 283
12, 701, 0.000000, 0.000000, 18, 0, 285
13, 759, 0.000000, 0.000000, 2, 0, 285
14, 813, 0.000000, 0.000000, 19, 0, 287
15, 868, 0.000000, 0.000000, 19, 0, 289
16, 922, 0.000000, 0.000000, 8, 0, 280
17, 977, 0.000000, 0.000000, 20, 0, 281
18, 1031, 0.000000, 0.000000, 19, 0, 284
19, 1087, 0.000000, 0.000000, 16, 0, 285
20, 1142, 0.000000, 0.000000, 25, 0, 282
21, 1197, 0.000000, 0.000000, 27, 0, 284
22, 1252, 0.000000, 0.000000, 12, 0, 286
23, 1307, 0.000000, 0.000000, 21, 0, 284
24, 1362, 0.000000, 0.000000, 9, 0, 283
25, 1420, 0.000000, 0.000000, 9, 0, 281
26, 1475, 0.000000, 0.000000, 21, 0, 286
27, 1530, 0.000000, 0.000000, 12, 0, 284
28, 1585, 0.000000, 0.000000, 8, 0, 284
29, 1640, 0.000000, 0.000000, 11, 0, 282
30, 1695, 0.000000, 0.000000, 12, 0, 286
31, 1750, 0.000000, 0.000000, 14, 0, 288
32, 1805, 0.000000, 0.000000, 13, 0, 282
33, 1860, 0.000000, 0.000000, 16, 0, 283
34, 1915, 0.000000, 0.000000, 18, 0, 285
35, 1971, 0.000000, 0.000000, 20, 0, 277
36, 2026, 0.000000, 0.000000, 16, 0, 284
37, 2081, 0.000000, 0.000000, 9, 0, 292
38, 2138, 0.000000, 0.000000, 10, 0, 282
39, 2193, 0.000000, 0.000000, 11, 0, 286
40, 2248, 0.000000, 0.000000, 10, 0, 286
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

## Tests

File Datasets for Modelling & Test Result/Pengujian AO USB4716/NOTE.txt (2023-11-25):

Pengujian AO dilakukan melalui tahapan/timelapse berikut
1. AI STM32 di run, di resume debug, kemudian AO USB4716 di run. sesaat AO USB4716 langsung memberi sinyal ramp
2. AO USB4716 saat >60s saturasi di 10VDC,
3. AO USB4716 akan turun saat >66s hingga 0s
4. STM32 me-eject/unmount sd card saat diffTime=150000ms

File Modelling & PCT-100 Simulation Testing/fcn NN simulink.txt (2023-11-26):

function u = fcn(e, e_1, e_2, lr_init, alpha)
    % initial condition
    persistent w_input v_hidden y_hidden delta2 hj ei_1 ei_2  lr n
    persistent v_hidden2 delta2_1 hj1
    if isempty(w_input)
%         w_input = zeros(3,3);
        w_input = rand(3,3);
        n = 0;
    end
    if isempty(v_hidden)   
%         v_hidden = zeros(1,3);
        v_hidden = rand(1,3);
%         v_hidden2 = rand(1,3);
    end
    if isempty(delta2)
        delta2 = zeros(1,3);
%         delta2_1 = zeros(1,3);
    end
    if isempty(hj)
        hj = [0;0;0];
        hj1 = [0;0;0];
    end
    if isempty(ei_1)
        ei_1 = 0;
    end
    if isempty(ei_2)
        ei_2 = 0;
    end
    if isempty(lr)
        lr = lr_init;
    end
    ei = e;
    x_input = [ei; ei_1; ei_2];
    % FORWARD PROPAGATION
    % Input layer to hidden layer
    for j_hiddenLayer = 1:3
        Sj = w_input(j_hiddenLayer,:) * x_input; % summing hidden neuron ke-j
        hj(j_hiddenLayer) = 1/(1 + exp(-1*Sj));
    end
    
    % hidden layer to output layer
    r = v_hidden * hj;
    u = 1/(1+exp(-1*r));

    % BACKWARD PROPAGATION: RETROPROPAGATION
%     alpha = 0.006;
    lr = lr + alpha*(ei)
%     lr = 20.6;
%     MSE = 0.5*(e_1^2)
    delta1 = ei*u*(1-u);
%     dey_deu = sign(ei);
    dey_deu =   1; %sign(ei);
    for j_hiddenLayer = 1:3
        v_hidden(j_hiddenLayer) = v_hidden(j_hiddenLayer) + lr * dey_deu * delta1 * hj(j_hiddenLayer);
        delta2(j_hiddenLayer) = delta1 * v_hidden(j_hiddenLayer) * hj(j_hiddenLayer) * (1 - hj(j_hiddenLayer));
        
        for i_inputLayer = 1:3
            w_input(j_hiddenLayer,i_inputLayer) = w_input(j_hiddenLayer,i_inputLayer) + lr * dey_deu * delta2(j_hiddenLayer) * x_input(i_inputLayer);
        end
    end
    
    ei_2 = ei_1;
    ei_1 = ei;
    w_input;
    v_hidden;
    n = n + 1;

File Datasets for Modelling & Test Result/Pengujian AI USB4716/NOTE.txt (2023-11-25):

pengujian ini dilakukan dengan timelapse berikut.
1. ramp start 3 detik dari void setup int main (mulai ramp dari diff=3000ms)
2. ramp akan terus naik selama 60s (hingga stuck di 10VDC saat diff=3000+60000=63000ms)
3. ramp akan steady saat berada pada 10VDC selama 3 detik (hingga diff=66000ms)
4. ramp akan terus turun hingga 0VDC, dan sd card stm akan eject/unmount pada 135000ms

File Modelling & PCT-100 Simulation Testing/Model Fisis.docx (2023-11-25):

Model Parametrik

(melihat peningkatan/penurunan permukaan air)

Model tangki proses:

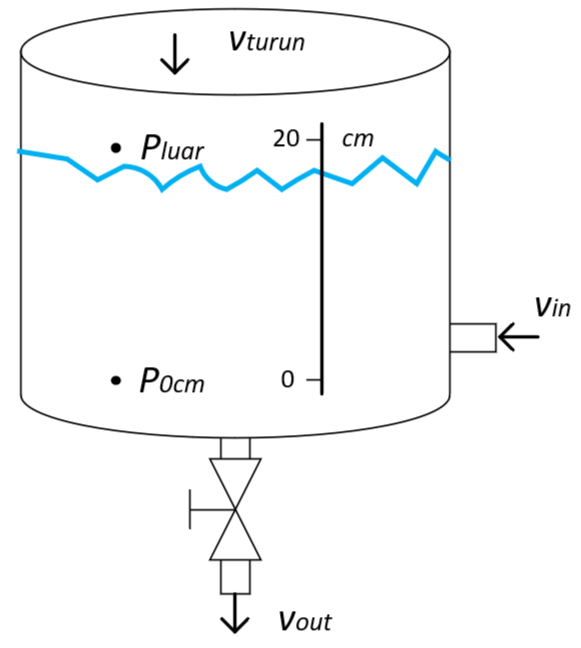
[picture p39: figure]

Persamaan tangki uniform dengan alas sebesar A dapat diturunkan menurut persamaan debit, yaitu

A_T h(t)=Q_(in) (t)-Q_(out) (t)

Hukum Bernoulli menyatakan jumlah tekanan, energi kinetic dan potensial per satuan volume memiliki nilai yang konstan sepanjang aliran fluida ideal. Penerapan hukum Bernoulli pada tangki air berlubang dirumuskan melalui persamaan berikut.

P_(luar) +1/2ρ v_(turun)^2 (t)+ρgh(t)=P_(0cm) +1/2ρ v_(out)^2 (t)+ρgh_(0cm) | (2.1)

Tekanan titik 1 dan titik 2 ialah tekanan atmosfer yang sama, sehingga P_(luar) -P_(0cm) =0

1/2ρ v_(turun)^2 (t)+ρgh(t)=1/2ρ v_(out)^2 (t) | (2.2)

v_(turun) ialah kecepatan permukaan fluida turun sehingga dapat dianalogikan dengan v_(turun) =(dh)/(dt) .

1/2ρ ((dh)/(dt))^2 +ρgh(t)=1/2ρ v_(out)^2 (t) | (2.3)

Sedangkan v_(out) dicari menggunakan persamaan kesetimbangan massa keluar-masuk:

Q_(in) (t)-A_(pipa) v_(out) (t)=A_(tabung) (dh)/(dt)

v_(out) (t)=(Q_(in) (t)-A_(tabung) (dh)/(dt))/(A_(pipa))

Substitusi ke persamaan 2.2 dan kalikan kedua ruas dengan ρ/2 :

((dh)/(dt))^2 +2gh(t)=((Q_(in) (t))/(A_(pipa))-(A_(tabung))/(A_(pipa))(dh)/(dt))^2

Karena selang fluida masukin sama diameternya dengan selang keluaran, A_(in) =A_(pipa) , sehingga (Q_(in) (t))/(A_(pipa))=v_(in) (t)

((dh)/(dt))^2 +20 h(t)=(v_(in) (t)-324(dh)/(dt))^2

Melalui penyederhanaan diperoleh:

-104975((dh)/(dt))^2 +648 v_(in) (dh)/(dt)+20 h(t)=v_(in)^2 | (2.4)

Persamaan diatas tidak memenuhi sifat superposisi, sehingga modelnya non linear, sehingga diperlukan teknik linearisasi agar mendapat model LTI yang beroperasi pada titik setimbangnya (equilibrium point).

Pendekatan linear terhadap model non linear:

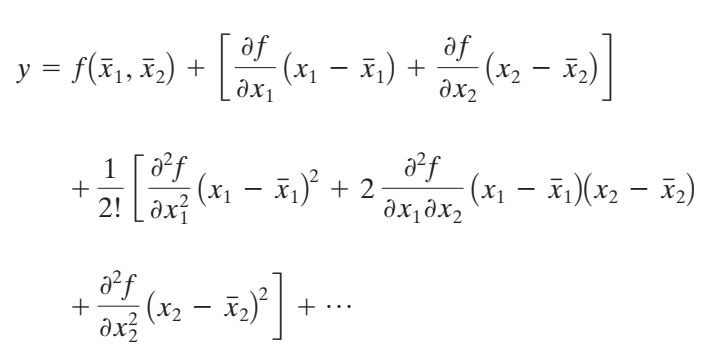
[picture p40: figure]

Model tangki bila diubah ke dalam state space, harus

Sinyal kontrol direpresentasikan u_(pompa) (t) , pompa memiliki gain flow K_(pompa) ,

v_(in) (t)=K_(pompa) u_(pompa) (t)

Jika digunakan model state space, vin ialah kecepatan fluida masuk tangki, h ialah ketinggian tangki

Model Parametrik

(mengabaikan peningkatan/penurunan permukaan air)

Ref: https://ximera.osu.edu/ode/main/drainingTank/drainingTank

Model tangki proses:

Persamaan tangki uniform dengan alas sebesar A dapat diturunkan menurut persamaan debit, yaitu

A_T h(t)=Q_(in) (t)-Q_(out) (t)

Hukum Bernoulli menyatakan jumlah tekanan, energi kinetic dan potensial per satuan volume memiliki nilai yang konstan sepanjang aliran fluida ideal. Penerapan hukum Bernoulli pada tangki air berlubang dirumuskan melalui persamaan berikut.

P_(luar) +1/2ρ v_(turun)^2 (t)+ρgh_(permukaan) (t)=P_(0cm) +1/2ρ v_(out)^2 (t)+ρgh_(0cm) | (2.1)

Tekanan titik 1 dan titik 2 ialah tekanan atmosfer yang sama, sehingga P_(luar) -P_(0cm) =0

ρg[h_(permukaan) (t)-h_(0cm) (t)]=1/2ρ v_(out)^2 (t) Dengan memisalkan h(t)=h_(permukaan) (t)-h_(0cm) (t) dan h_(0cm) =0m , diperoleh: | (2.2)

v_(out) =√(2g h(t))

Q_(out) =A_(pipa) √(2g h(t))

h(t)=1/(2g)((Q_(out))/(A_(pipa)))^2

v_(out) dapat pula dicari menggunakan persamaan kesetimbangan massa keluar-masuk:

Q_(in) (t)-A_(pipa) √(2g h(t))=A_(tabung) (dh)/(dt)

A_(pipa) v_(in) (t)-A_(pipa) √(2g h(t))=A_(tabung) (dh)/(dt)

v_(in) (t)-√(2g h(t))=(A_(tabung))/(A_(pipa)) (dh)/(dt)

Permodelan plant di Simulink:

v_(in) (t)-√(2g h(t))=(A_(tabung))/(A_(pipa)) (dh)/(dt)

(A_(pipa))/(A_(tabung)) (v_(in) (t)-√(2g h(t)))= (dh)/(dt)

H=∫ (dh)/(dt) dt=∫ (A_(pipa))/(A_(tabung)) (v_(in) (t)-√(2g h(t))) dt

Melalui penyederhanaan diperoleh:

v_(in) (t)-√(20 h(t))=324 (dh)/(dt) | (2.4)

Persamaan diatas tidak memenuhi sifat superposisi, sehingga modelnya non linear, sehingga diperlukan teknik linearisasi agar mendapat model LTI yang beroperasi pada titik setimbangnya (equilibrium point).

Pendekatan linear terhadap model non linear didasarkan pada ekspansi deret taylor. Suku dengan pangkat/orde tinggi dapat diabaikan karena nilainya terlampau kecil. Fungsi nonlinear ini diselesaikan menggunakan deret taylor:

y=f(x)=f(x_0 )+(df)/(dx)(x-x_0 )+…(diabaikan)

Dimana x=h , f(x)=f(h)=√h , x_0 =h_0

f(h)=f(h_0 )+(df)/(dh)(h-h_0 )

√h=√(h_0)+(d √h)/(dh)(h-h_0 )

√h=√(h_0)+1/(2√(h_0))(h-h_0 )

Substitusikan ke persamaan 2.4

v_(in) (t)-√(2g) (√(h_0)+1/(2√(h_0))(h-h_0 ))=(A_(tabung))/(A_(pipa)) (dh)/(dt)

Untuk t=0s, v_(in) (0)=v_(in,0) =√(20 h_0) . Lalu substitusikan ke persamaan sebelumnya

v_(in) (t)-v(0)-(√(2g))/(2√(h_0))(h-h_0 )=(A_(tabung))/(A_(pipa))(dh)/(dt)

(A_(tabung))/(A_(pipa))(dh)/(dt)+(√(2g))/(2√(h_0))(h-h_0 )=v_(in) (t)-v_(in) (0)

Memisalkan h^(') (t)=h-h_0 , v_(in)^(') (t)=v_(in) (t)-v_(in) (0)

(A_(tabung))/(A_(pipa))(dh')/(dt)+C/(2√(h_0))h'(t)=v_(in)^(') (t)

τ(dh')/(dt)+h'(t)=kv_(in)^(') (t)

Dimana τ=(2√(h_0))/C(A_(tabung))/(A_(pipa)) dan k=(2√(h_0))/C

Persamaan ini diubah dengan transformasi laplace menjadi:

τ sH'(s)+H'(s)=k V_(in)^(') (s)

H^(') (s)=k/(τs+1)V_(in)^(') (s)

Jika diberikan step input V_(in)^(') (s)=M/s ,

H^(') (s)=k/(τs+1)M/s

Untuk mengubahnya Kembali ke domain waktu, digunakan pembagian pecahan (partial fraction) diperoleh:

H^(') (s)=(k M)/(s(τs+1))=(C_1)/s+(C_2)/(τs+1)

Untuk koefisien s=0 : C_1 =kM

Untuk koefisien s^1 : C_1 τ+C_2 =0, C_2 =-τkM

H^(') (s)=(kM)/s-(τkM)/(τs+1)

H^(') (s)=(kM)/s-(kM)/(s+1/τ)

Inverse laplace:

L^(-1) {H^(') (s)}=L^(-1) {(kM)/s}-L^(-1) {(kM)/(s+1/τ)}

h^(') (t)=kM-kM e^(-t/τ)

h^(') (t)=kM(1-e^(-t/τ) )

Untuk mencari nilai k dan τ perlu dilakukan identifikasi system terhadap sampling sebelumnya:

τ(dh'(t))/(dt)+h'(t)=kv_(in)^(') (t-θ)

Parameter yang akan diidentifikasi: [k, τ,θ]

Maka, persamaan differensial diatas menjadi:

h^(') (t)=kM(1-e^(-((t-θ))/τ) )

Model tangki bila diubah ke dalam state space, harus dinyatakan dalam bentuk berikut. (Buku Control System Design, hal.49)

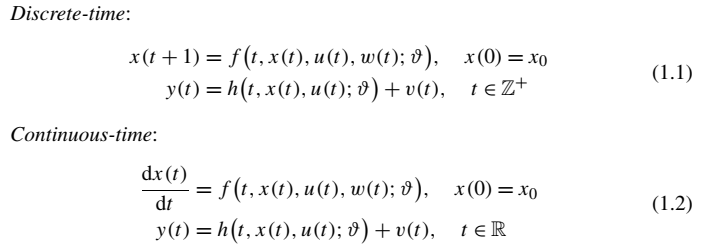
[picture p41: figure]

System dikatakan linear bila memenuhi prinsip superposisi, dikatakan time-invariant bila respon terhadap waktu input merupakan translasi waktu dari respon asli. Dari system LTI, persamaan 1.1 dan 1.2 diilustrasikan dengan state space berikut.

(dx(t))/(dt)=Ax(t)+Bu(t)

y(t)=Cx(t)+Du(t)

Karena model state space merupakan gabungan persamaan differensial orde 1, solusi persamaan dapat ditentukan dengan matrix eksponensial sebagai

e^(At) =I+∑_(i=1)^(∞) 1/(i!)A^i t^i

Solusi eksplisit linear state equation:

x(t)=e^(A(t-t_0 )) x_0 +∫_(t_0)^t e^(A(t-τ)) Bu(τ) dτ

Kesetimbangan massa dalam tangki dapat dibuat state variable: (Keesman, system identification. hal.7 )

V(t) :volume air dalam tangki

v_(in) (t):volume air masuk tanki (inflow)

v_(out) (t):volume air keluar tangki (outflow)

Dari hasil linearisasi model orde 1, diperoleh

τ(dV(t))/(dt)+V(t)=kV_(in) (t)

State space:

V=(dV(t))/(dt)=-1/τV(t)+kV_(in) (t)

h(t)=1/AV(t)

system identification:

1. Metode ziegler nichols
2. Metode strejc

Model strejc diketahui dengan memberikan step input lalu menarik garis lurus untuk menentukan T_U dan T_N . Nilai τ dari rasio T_U dan T_N

τ=(T_U)/(T_N)

Consider an approximation of a process by the nth order system

G(s)=Z/((Ts + 1)^n) e^(-T_d s) (6.38)

where Z is the process gain, T time constant, Td time delay, and n the system

order that all are to be estimated.

Consider now properties of the normalised step response if Td = 0 (Fig. 6.5)

G(s)=1/((Ts + 1)^n) (6.39)

The following facts will be used for the derivation:

1. The tangent of the step response in the inflexion point [t_i ,y_i ] is given by the equation of a line p : y = a + bt ,
2. The line p passes through points [T_u ,0],[T_u + T_n ,1],[t_i ,y_i ] . The following holds: b =1/(Tn) and a = -T_u b ,
3. The slope of the line p is given as b = y(t_i ) ,
4. y(t_i ) = 0 (inflexion point).

The step response can by obtained by the means of the inverse Laplace transform and is given as

y(t)= 1 - e^(-t/T) ∑_(k=0)^(n-1) 1/(k!)(t/T)^k

(6.40)

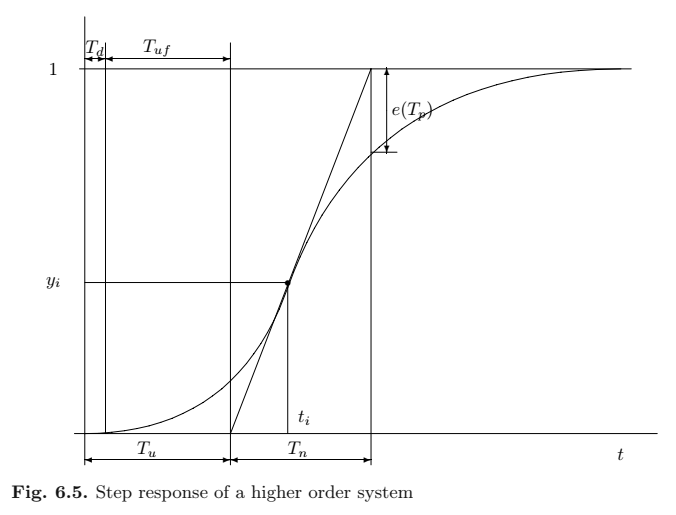
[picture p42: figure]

We calculate the first and the second derivative of the output y with respect to time

y(t)=1/(T^n (n - 1)!) t^(n-1) e^(-t/T) (6.41)

y(t)=1/(T^n) [(t^(n-2))/((n-2)!) -1/T(t^(n-1))/((n-1)!)]e^(-t/T) (6.42)

In the inflexion point holds ¨ y(ti) = 0, hence

t_i = T(n - 1) (6.43)

Evaluating y at time ti gives

y(t_i )=((n - 1)^(n-1))/(T(n - 1)!) e^(-(n-1)) (6.44)

It can be seen from the figure that y(t_i )=1/(Tn) , thus

T/(Tn)=((n - 1)^(n-1))/((n - 1)!) e^(-(n-1)) =g(n) (6.45)

We can see that this function depends only on n.

Further, it can be shown that the relation between Tu and Tn is again only a function of n

(T_u)/(T_n)=e^(-(n-1)) [((n-1)^n)/((n-1)!)+∑_(k=0)^(n-1) 1/(k!)(n-1)^k ]-1=f(n)

The identification procedure is then as follows:

1. The values of Z = y(∞), Tus,Tn are read from the step response,
2. The quotient fs = Tus/Tn is calculated,
3. The degree n0 is chosen from the table in such a way that the following holds

f(n_0 )≤f_s <f(n_0 +1)

4. Time delay Td can be determined as the difference between the real and theoretical time Tu

T_d =[f_s -f(n_0 )]T_n

because T_u =T_n f(n) ,

5. The process time constant T can be read from the row of g(n) for the corresponding n0. T is obtained from the definition of g

T=T_n g(n_0 ).

3. Metode viteckova orde 1
4. Metode viteckova orde 2
5. Metode latzel
6. Metode Harriot

Metode Harriott (Jakoubek, 2009) mencoba untuk menyimulasikan sistem dengan menggunakan model orde 2 yang memungkinkan untuk menyertakan delay waktu. Fungsi transfer model yang dihasilkan dapat dituliskan sebagai berikut:

G_H (s)=K/((τ_(H1) + 1) (τ_(H2) +1))e^(-T_(dH) s) (2.15)

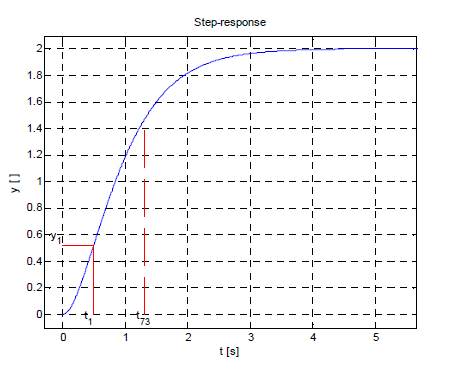
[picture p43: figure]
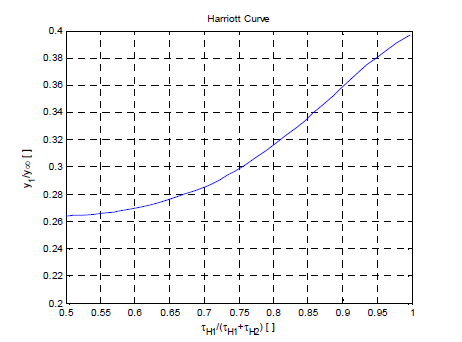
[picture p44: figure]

Gambar 2-5 Harriot's Curve

Berikut adalah tahapan untuk mendapatkan parameter τ_(H1) , τ_(H2) dan T_(dH) :

### 1.1.1 Menentukan jumlah dari parameter τ_(H1) dan τ_(H2)

Jumlah dari parameter τ_(H1) dan τ_(H2) dapat dirumuskan sebagai berikut:

τ_(H1) + τ_(H2) = (t_73)/1.3 (2.16)

Dengan t_73 adalah waktu saat respons system berada pada kondisi 73% mendekati luaran steady state ( Y_(ss) ).

### 1.1.2 Menentukan parameter t_1 dan Y_1

Parameter t_1 parameter t_1 diperlukan untuk menghitung parameter Y_1 , yang diperoleh dari respon sistem yang telah diidentifikasi. Rumus untuk menghitung parameter t_1 adalah sebagai berikut:

t_1 = (τ_(H1) + τ_(H2))/2 (2.17)

### 1.1.3 Menentukan parameter pada kurva Harriot

Pada kurva Harriott, parameter yang diberikan terletak pada sumbu X dan Y. Parameter yang ditunjukkan pada sumbu Y adalah sebagai berikut:

(Y1)/(Y∞)[ ] atau (Y1)/(Yss) (2.18)

Setelah menentukan parameter (Y1)/(Y∞)[ ] pada sumbu Y, garis dapat ditarik untuk mendapatkan parameter τ_(H1) / (τ_(H1) + τ_(H2) ) pada sumbu X. Parameter ini merupakan koordinat sumbu X pada kurva Harriott. Dengan demikian, kita dapat menggambarkan kurva Harriott dengan menggunakan parameter yang diperoleh pada kedua sumbu tersebut.

### 1.1.4 Menentukan parameter τ_(H1)

Untuk mencari parameter τ_(H1) maka persamaan nilai τ_(H1) / (τ_(H1) + τ_(H2) ) dapat diasumsikam pada kurva Harriot sebagai x, kemudian substitusikan persamaan 2.19

(τ_(H1))/((τ_(H1) + τ_(H2) ))=x (2.19)

(τ_(H1))/((t_73)/1.3)=x → τ_(H1) =x* (t_73)/1.3 (2.20)

### 1.1.5 Menentukan Parameter τ_(H2)

Untuk mendapatkan parameter , subsitusikan persamaan 2.19 pada persamaan 2.22 sehingga diperoleh:

τ_(H1) + τ_(H2) = (t_73)/1.3 (2.21)

x* (t_73)/1.3 + τ_(H2) = (t_73)/1.3 (2.22)

τ_(H2) = (t_73)/1.3-(x*(t_73)/1.3 ) (2.23)

### 1.1.6 Menentukan parameter T_(dH)

T_(dH) adalah time delay yang dapat di metode Harriot dirumuskan sebagai berikut:

T_(dH) = 1.937 t_33 -0.937t_70 (2.24)

Untuk menggunakan hasil parameter τ_(H1) , τ_(H2) , dan T_(dH) Parameter tersebut dapat memasukkannya ke dalam persamaan 2.24. Jika nilai waktu t_33 dan t_70 kurang dari 0 atau bernilai negatif, maka sistem dianggap tidak memiliki time delay. Dengan menggunakan hasil parameter tersebut dalam persamaan 2.24, sehingga dapat ditentukan kinerja sistem tersebut.

Untuk mendapatkan fungsi alih sistem, digunakan respons saat set poin adalah 5 volt atau 50% dari flow rate Gambar 3.8 menunjukkan respon level pada set point 50%. Dari respons tersebut, diperoleh nilai keluaran steady state pada ketinggian 1,939, yang diperoleh dari rata-rata seluruh data keluaran steady state. Berdasarkan respons pada Gambar 3.8, diperoleh gain overall respons pada persamaan berikut.

Y_(ss) =1.939

X_(ss) =2

K= (Y_(ss))/(X_(ss))= 1.95/1.89=1.03 | (3.10)

Jakoubek mengembangkan 7 metode untuk mengidentifikasi plant atau sistem kontrol. Salah satu metode yang dapat digunakan dalam pendekatan model matematika plant adalah metode Harriott. Pemilihan metode terbaik dapat dilakukan dengan menggunakan validasi. Salah satu metode validasi yang dapat digunakan adalah ISE (Integral Square Error). Semakin kecil nilai ISE, maka semakin baik fungsi alih yang dibuat. Dengan menggunakan pendekatan sistem model matematika plant proses level dan berdasarkan respons pada Gambar 3.8, dapat diperoleh nilai ISE yang sesuai

t33=7

t70=16

t73=1.809

Sehingga diperoleh parameter:

T_(dH) =1.937 t_33 -0.937t_70 | (3.11)

T_(dH) =-0.432 | (3.12)

τ_(H1) + τ_(H2) = (t_73)/1.3

τ_(H1) + τ_(H2) = 1.809/1.3=1.39 | (3.13)

t_1 = (τ_(H1) + τ_(H2))/2= 1.39/2=0.695 →y_1 =0.77 | (3.14)

Berdasarkan kurva Harriott pada Gambar 2.5, diperoleh nilai:

(y_1)/(Y_(ss))=0.77/1.939=0.397 → (τ_(H1))/((τ_(H1) + τ_(H2)))=0.561 | (3.15)

(τ_(H1))/((τ_(H1) + τ_(H2)))=x → = τ_(H1) =x.(t_73)/1.3 | (3.16)

τ_(H1) =0.561 x 1.89/1.3=0.815 | (3.17)

τ_(H2) = (t_73)/1.3-(x* (t_73)/1.3)= 1.39- 0.815=0.575 | (3.18)

Karena parameter delay bernilai negatif, sehingga nilai delay tidak dianggap. Fungsi alih untuk metode Harriot adalah:

GH(s)=K/((τH1s+1)(τH2s+1)) e^(-TdHs)

GH(s)=1.03/((0.815s+1)(0.575s+1))

GH(s)=1.03/(0.468s^2 +1.39s+1) | (3.19)

Penelitian ini mengukur respon dari model terhadap masukan sinyal uji untuk menentukan kesesuaiannya dengan real plant dalam proses identifikasi. Hasil percobaan menunjukkan bahwa ISE sebesar dan model matematikanya merupakan pendekatan orde 2, yang umumnya sesuai dengan sistem orde 2 pada dunia industri.

Spesifikasi respon:

1. Steady state condition:

Yss = 3.429242569267122

Yss5% lower = 3.2577804408037654

Yss5% upper = 3.600704697730478

Yss2% lower = 3.360657717881779

Yss2% upper = 3.4978274206524644

Yss1% lower = 3.3949501435744507

Yss1% upper = 3.463534994959793

2. Karakteristik respon:

Td = 1.2785508632659912 ; Y(Td) = 2.2774461779188386

Tr = 3.199901580810547 ; Y(Tr) = 3.6318146714788804

Tp = 4.115921497344971 ; Y(Tp)= 3.8241972880051995

Max Overshoot(%) = 11.517258133841644

Ess = -0.001281696312633862

Ts1% = 35.595086097717285

Ts2% = 6.793642044067383

Ts5% = 5.027848958969116

System Identification:

1. 1st order vitechkova

G_(v1) =(K_(v1))/(T_(v1) s+1)e^(-T_(dv1) s)

Kv1 = 0.817411096174997

Tdv1 = 0.41778553390502937

Tv1 = 1.4622697019577027

G_(v1) =0.8174/(1.4623 s+1)e^(-0.4178 s)

2. 2nd order vitechkova

G_(v2) =(K_(v2))/((T_(v2) s+1)^2)e^(-T_(dv2) s)

k33% = 7 ; y33% = 0.0

k70% = 16 ; y70% = 3.371502150382973

Kv2 = 0.817411096174997

Tdv2 = -0.09782603168487558

Tv2 = 0.932563970565796

G_(v2) =0.8174/((0.9326 s+1)^2)e^0.0978 (problem: pangkat time delay+)

3. Latzel

G_L (s)=K/((τ_L s+1)^n)

Klatzel = 0.817411096174997

n=2

tauL = 2.2832144310474396

miu = 0.10208216929967592

G_L (s)=0.8174/((2.2832 s+1)^2)

4. Harriot

G=K/((τ_(H1) s+1)(τ_(H2) s+1))e^(-T_(dh) s)

t73 = 2.310636520385742

yHarriot = 0.0

t1 = 0.8887063539945161

y(t1)= 0.0

TdH = -0.09782603168487558

Harriot tidak bisa dimodelkan karena yHarriot<0.26, karena respon underdamped

5. Smith

G_(SM) =K/((τ_(SM1) s+1)(τ_(SM2) s+1))

Dengan τ_(SM1) =τζ+τ√(ζ^2 -1) dan τ_(SM2) =τζ-τ√(ζ^2 -1)

G_(SM) =K/(τ^2 s^2 +2τζs+1)

Ksmith = 0.817411096174997

denum a=τ^2 = 0.038709501241328326

denum b=2τζ= 1.5739784240722656

tau = 0.1967473030090332

zeta = 4

x_smith = 0.26292361533558406 akan digunakan untuk mencari ySmith untuk menentukan tau dan zeta, diperoleh:

G_(SM) =0.8174/(0.0387s^2 +1.574s+1)

6. Sundaresen & Krishnaswamy

G_(SK) =K/(τ_(SK) s+1)e^(-T_(dSK) s)

K_(krisnaswamy) = 0.817411096174997

tauSK = 1.0317201042175295

TdSK = 0.7044448280334474

G_(SK) =0.8174/(1.0317s+1)e^(-0.7044s)

7. Strejc τ>0 , approximated by nth order model

G_(ST2) =K/((τ_(ST) s+1)^n)

τ_(ST) = 2.310636520385742

τ=(Tu)/(Tn)= 0.12568148408085394

t_i = 2.310636520385742

y_i (t_i ) = 3.371502150382973

G_(ST2) =0.8174/((2.3106s+1)^2)

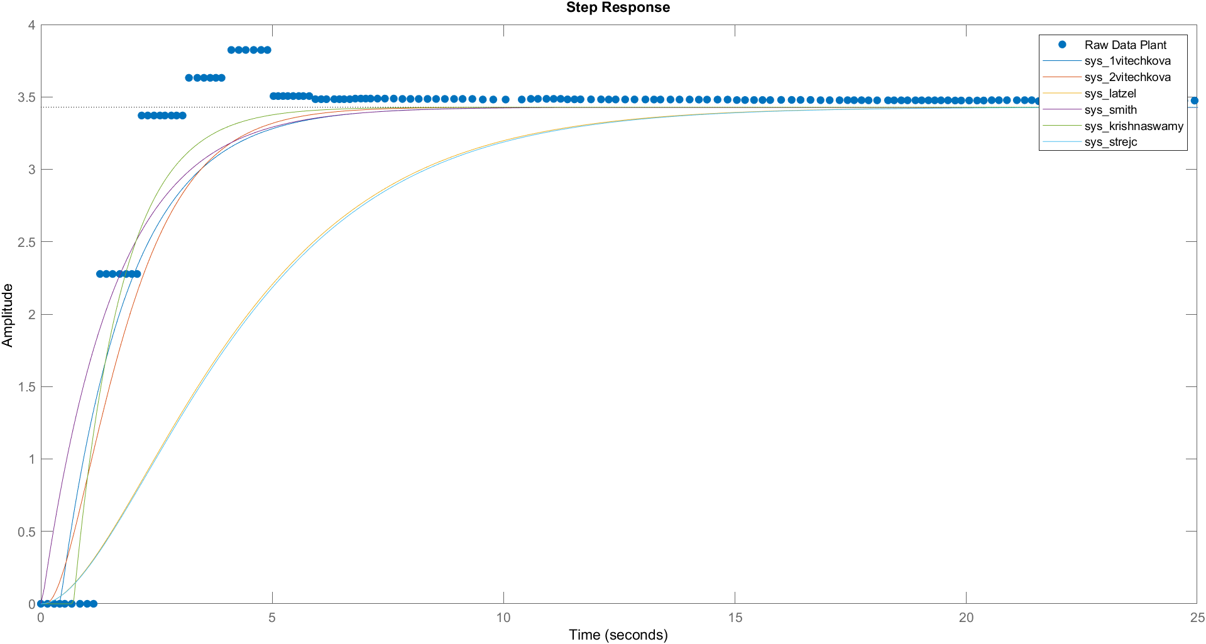
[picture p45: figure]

Permodelan valve

Merujuk pada datasheet valve Burkert 2835,

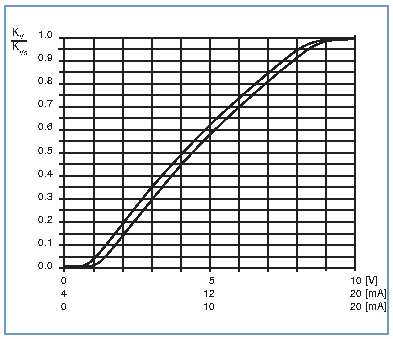
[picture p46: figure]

Gambar 1. Kurva karakteristik proportional valve.

Dimana

K_V : koefisien flow air (m3/h), diukur pada ∆P=1

K_(VS) : nilai laju flow air, diukur pada ∆P=1 dan T=20°C

K_V =Q√(ρ/(1000 ∆P))

Q=K_V √((1000 ∆P)/ρ)

Pada buku Chemical_Process_Dynamics_and_Controls_(Woolf) section 3.10: Valves - Modeling Dynamics, persamaan umum flow dari valve:

F=C_V f(x)√((∆P)/(sg))

Dimana

F : laju flow

Cv : koefisien valve, flow dalam gallon/min dengan ∆P=1 psi

∆P_V : pressure drop valve

sg : specific gravity fluida

X: franction valve terbuka atau valve ‘lift’, x=1 untuk flow max

F(x) : flow characteristics

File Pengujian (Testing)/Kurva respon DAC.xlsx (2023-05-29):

STEP %pwm | duty cycle bit | Vout mosfet | seharusnya | Vmosfet ini diukur saat Vpsu=27.0 V
0 | 0 |  | 0 | Vout mosfet
10 | 409.6 |  | 2.4 | 0.058
20 | 819.2 |  | 4.8 | 1.471
30 | 1228.8 |  | 7.2 | 4.27
40 | 1638.4 |  | 9.6 | 7.09
50 | 2048 |  | 12 | 9.9
60 | 2457.6 |  | 14.4 | 12.72
70 | 2867.2 |  | 16.8 | 15.54
80 | 3276.8 |  | 19.2 | 18.36
90 | 3686.4 |  | 21.6 | 21.2
100 | 4096 |  | 24 | 23.98
 |  |  |  | 23.99

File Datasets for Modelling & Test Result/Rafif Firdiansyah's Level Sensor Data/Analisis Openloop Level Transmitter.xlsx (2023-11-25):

n | volt flow | volt level floating | volt pot | timenow | 10-volt pot | level (cm) | Column1 | level LT (cm)
1 | 0.009613183795 | -0.296177615 | 9.946593423 | 1672578962 | 0.05340657664 |  | 4.241424 | 0.01652542373
2 | 0.009613183795 | -0.296177615 | 9.946593423 | 1672578962 | 0.05340657664 |  | 4.241424 | 0.03305084746
3 | 0.009613183795 | -0.296177615 | 9.946593423 | 1672578962 | 0.05340657664 |  | 4.241424 | 0.04957627119
4 | 0.009613183795 | -0.296177615 | 9.946593423 | 1672578962 | 0.05340657664 |  | 4.241424 | 0.06610169492
5 | 0.009613183795 | -0.296177615 | 9.946593423 | 1672578962 | 0.05340657664 |  | 4.241424 | 0.08262711864
6 | 0.009613183795 | -0.296177615 | 9.946593423 | 1672578962 | 0.05340657664 |  | 4.241424 | 0.09915254237
7 | 0.009613183795 | -0.296177615 | 9.946593423 | 1672578963 | 0.05340657664 |  | 4.241424 | 0.1156779661
8 | 0.009613183795 | -0.296177615 | 9.946593423 | 1672578963 | 0.05340657664 |  | 4.241424 | 0.1322033898
9 | 0.009613183795 | -0.296177615 | 9.946593423 | 1672578963 | 0.05340657664 |  | 4.241424 | 0.1487288136
10 | 0.009613183795 | -0.296177615 | 9.946593423 | 1672578963 | 0.05340657664 |  | 4.241424 | 0.1652542373
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

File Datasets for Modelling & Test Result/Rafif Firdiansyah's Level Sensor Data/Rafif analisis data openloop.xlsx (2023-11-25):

n | volt flow | volt level floating | volt pot | timenow | 10-volt pot | level (cm)
1 | 0.009613183795 | -0.296177615 | 9.946593423 | 1672578962 | 0.05340657664 | 0.0000000000 | 0.14
2 | 0.009613183795 | -0.296177615 | 9.946593423 | 1672578962 | 0.05340657664 | 0.0000130617
3 | 0.009613183795 | -0.296177615 | 9.946593423 | 1672578962 | 0.05340657664 | 0.0000130617
4 | 0.009613183795 | -0.296177615 | 9.946593423 | 1672578962 | 0.05340657664 | 0.0000130617
5 | 0.009613183795 | -0.296177615 | 9.946593423 | 1672578962 | 0.05340657664 | 0.0000130617
6 | 0.009613183795 | -0.296177615 | 9.946593423 | 1672578962 | 0.05340657664 | 0.0000130617
7 | 0.009613183795 | -0.296177615 | 9.946593423 | 1672578963 | 0.05340657664 | 0.0000130617
8 | 0.009613183795 | -0.296177615 | 9.946593423 | 1672578963 | 0.05340657664 | 0.0000130617
9 | 0.009613183795 | -0.296177615 | 9.946593423 | 1672578963 | 0.05340657664 | 0.0000130617
10 | 0.009613183795 | -0.296177615 | 9.946593423 | 1672578963 | 0.05340657664 | 0.0000130617
11 | 1.516594186 | -0.296177615 | 9.946593423 | 1672578963 | 0.05340657664 | 0.0000130617
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

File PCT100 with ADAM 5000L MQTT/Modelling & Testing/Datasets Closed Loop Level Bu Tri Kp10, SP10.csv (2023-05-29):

k | timestamp | PV_level (cm) | PV_flow (VDC)
1 | 0.0009982585906982422 | 4.28555357802478 | 0.0
2 | 0.13236498832702637 | 4.28555357802478 | 0.0
3 | 0.28404808044433594 | 4.28555357802478 | 0.0
4 | 0.4086267948150635 | 4.28555357802478 | 0.0
5 | 0.5492508411407471 | 4.2902380872426855 | 0.0
6 | 0.6869685649871826 | 4.2902380872426855 | 0.0
7 | 0.784710168838501 | 4.2902380872426855 | 0.0
8 | 0.8994350433349609 | 4.2902380872426855 | 0.0
9 | 1.0380289554595947 | 4.2902380872426855 | 0.0
10 | 1.147740125656128 | 4.2902380872426855 | 0.0
11 | 1.2534830570220947 | 4.2902380872426855 | 0.0
12 | 1.4000608921051025 | 4.2902380872426855 | 2.6113280673599197
13 | 1.5666234493255615 | 4.2923200913395325 | 2.6113280673599197
14 | 1.6793136596679688 | 4.2923200913395325 | 2.6113280673599197
15 | 1.8189458847045898 | 4.2923200913395325 | 2.6113280673599197
16 | 1.948451280593872 | 4.2923200913395325 | 2.6113280673599197
17 | 2.08951735496521 | 4.2923200913395325 | 2.6113280673599197
18 | 2.2121920585632324 | 4.2923200913395325 | 3.380345854940146
19 | 2.336094379425049 | 4.2923200913395325 | 3.380345854940146
20 | 2.451547145843506 | 4.2923200913395325 | 3.380345854940146
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

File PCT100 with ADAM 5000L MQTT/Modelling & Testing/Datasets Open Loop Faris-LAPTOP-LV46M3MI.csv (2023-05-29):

k | timestamp | PV_level (cm) | PV_flow (VDC) | dPVflow | dt | Q_FT (lt/min)
1 | 0.0009982585906982422 | 4.809177608381744 | -0.00015259021896696368 | -0.00015259021896696368 | 1678375267.0230227 | -7.143355676068225e-14
2 | 0.13563776016235352 | 4.809177608381744 | -0.00015259021896696368 | 0.0 | 1678375267.0230227 | -7.143355676068225e-14
3 | 0.2812495231628418 | 4.809177608381744 | -0.00015259021896696368 | 0.0 | 1678375267.0230227 | -7.143355676068225e-14
4 | 0.38198018074035645 | 4.809177608381744 | -0.00015259021896696368 | 0.0 | 1678375267.0230227 | -7.143355676068225e-14
5 | 0.5106353759765625 | 4.809177608381744 | -0.00015259021896696368 | 0.0 | 1678375267.0230227 | -7.143355676068225e-14
6 | 0.6113662719726562 | 4.809177608381744 | -0.00015259021896696368 | 0.0 | 1678375267.0230227 | -7.143355676068225e-14
7 | 0.7490007877349854 | 4.809177608381744 | -0.00015259021896696368 | 0.0 | 1678375267.0230227 | -7.143355676068225e-14
8 | 0.8796508312225342 | 4.809177608381744 | -0.00015259021896696368 | 0.0 | 1678375267.0230227 | -7.143355676068225e-14
9 | 1.0183141231536865 | 4.809177608381744 | -0.00015259021896696368 | 0.0 | 1678375267.0230227 | -7.143355676068225e-14
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

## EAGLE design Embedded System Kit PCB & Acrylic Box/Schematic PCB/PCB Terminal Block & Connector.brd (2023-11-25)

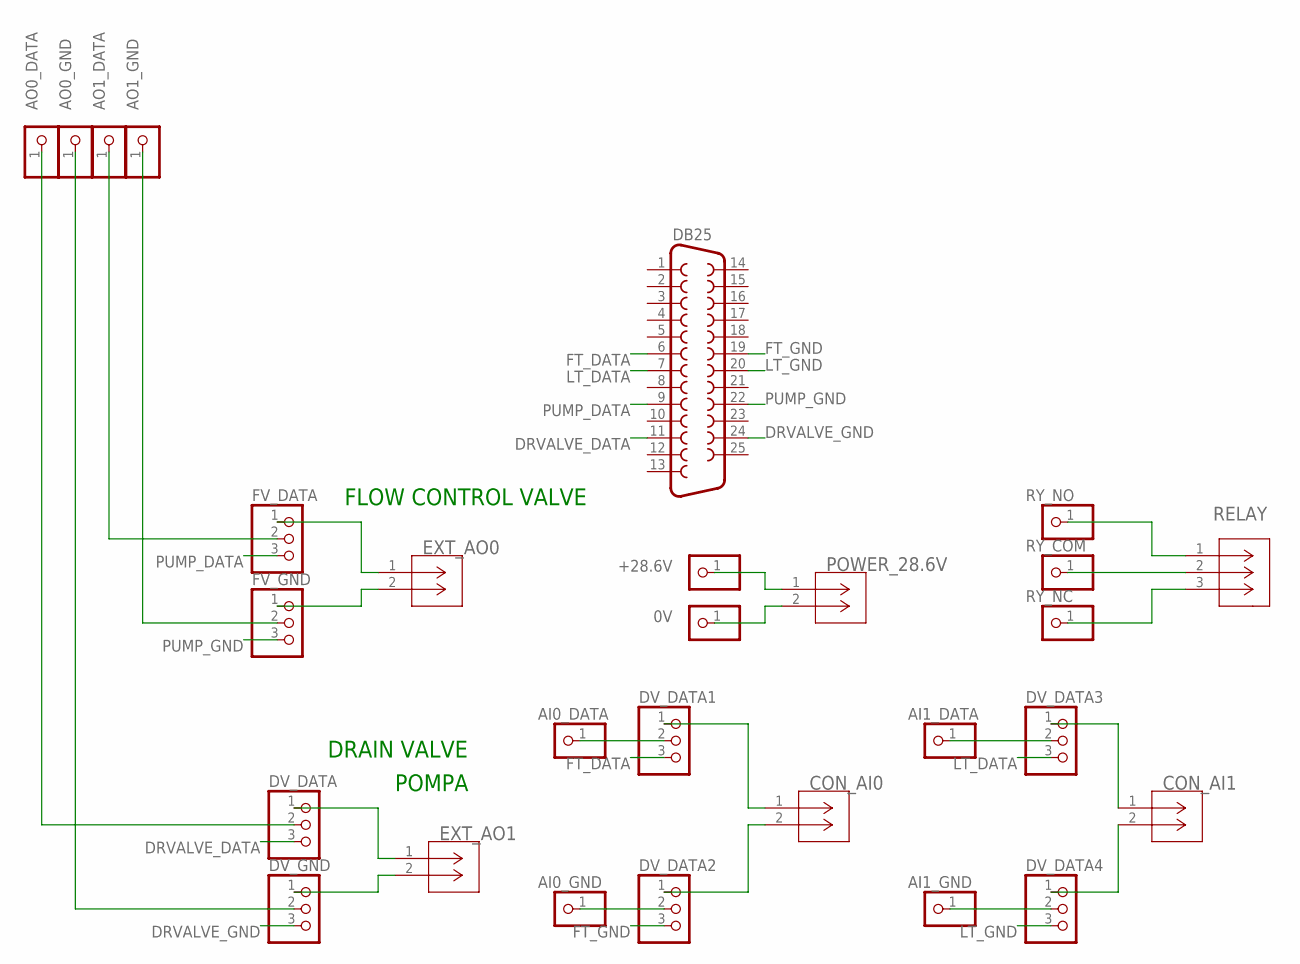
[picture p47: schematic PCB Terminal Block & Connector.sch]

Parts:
0V: PINHD-1X1; 1X01
+28.6V: PINHD-1X1; 1X01
AI0_DATA, AI0_GND, AI1_DATA, AI1_GND: PINHD-1X1; 1X01
AO0_DATA, AO0_GND, AO1_DATA, AO1_GND: PINHD-1X1; 1X01
CON_AI0, CON_AI1: KF8500-8.5-2P; CONN_KF8500-8.5-2P_CKE
DB25: F25H
DV_DATA, DV_DATA1, DV_DATA2, DV_DATA3, DV_DATA4: PINHD-1X3; 1X03
DV_GND: PINHD-1X3; 1X03
EXT_AO0, EXT_AO1: KF8500-8.5-2P; CONN_KF8500-8.5-2P_CKE
FV_DATA: PINHD-1X3; 1X03
FV_GND: PINHD-1X3; 1X03
POWER_28.6V: KF8500-8.5-2P; CONN_KF8500-8.5-2P_CKE
RELAY: KF8500-8.5-4P; CONN4_KF8500_1X4_1398X472_CKE
RY_COM: PINHD-1X1; 1X01
RY_NC: PINHD-1X1; 1X01
RY_NO: PINHD-1X1; 1X01

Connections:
AO0_DATA: AO0_DATA.1, DV_DATA.2
AO0_GND: AO0_GND.1, DV_GND.2
AO1_DATA: AO1_DATA.1, FV_DATA.2
AO1_GND: AO1_GND.1, FV_GND.2
DRVALVE_DATA: DB25.11, DV_DATA.3
DRVALVE_GND: DB25.24, DV_GND.3
EXT_AO2: DV_DATA.1, EXT_AO1.1
FT_DATA: DB25.6, DV_DATA1.3
FT_GND: DB25.19, DV_DATA2.3
LT_DATA: DB25.7, DV_DATA3.3
LT_GND: DB25.20, DV_DATA4.3
unnamed: +28.6V.1, POWER_28.6V.1
unnamed: 0V.1, POWER_28.6V.2
unnamed: EXT_AO0.2, FV_GND.1
unnamed: CON_AI0.1, DV_DATA1.1
unnamed: CON_AI1.1, DV_DATA3.1
unnamed: AI0_DATA.1, DV_DATA1.2
unnamed: AI0_GND.1, DV_DATA2.2
unnamed: CON_AI0.2, DV_DATA2.1
unnamed: EXT_AO0.1, FV_DATA.1
unnamed: CON_AI1.2, DV_DATA4.1
unnamed: AI1_DATA.1, DV_DATA3.2
unnamed: DV_GND.1, EXT_AO1.2
unnamed: RELAY.2, RY_COM.1
unnamed: AI1_GND.1, DV_DATA4.2
unnamed: RELAY.3, RY_NC.1
unnamed: RELAY.1, RY_NO.1
PUMP_DATA: DB25.9, FV_DATA.3
PUMP_GND: DB25.22, FV_GND.3

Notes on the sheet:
FLOW CONTROL VALVE
DRAIN VALVE
POMPA

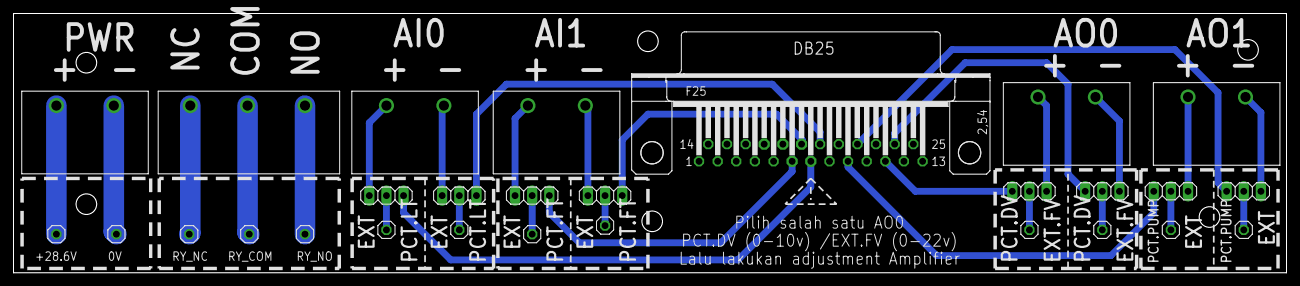
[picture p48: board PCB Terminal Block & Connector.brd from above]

Board: 2 copper layers, 188.6 x 38.4 mm, 28 parts (0 on the bottom side), 29 nets.

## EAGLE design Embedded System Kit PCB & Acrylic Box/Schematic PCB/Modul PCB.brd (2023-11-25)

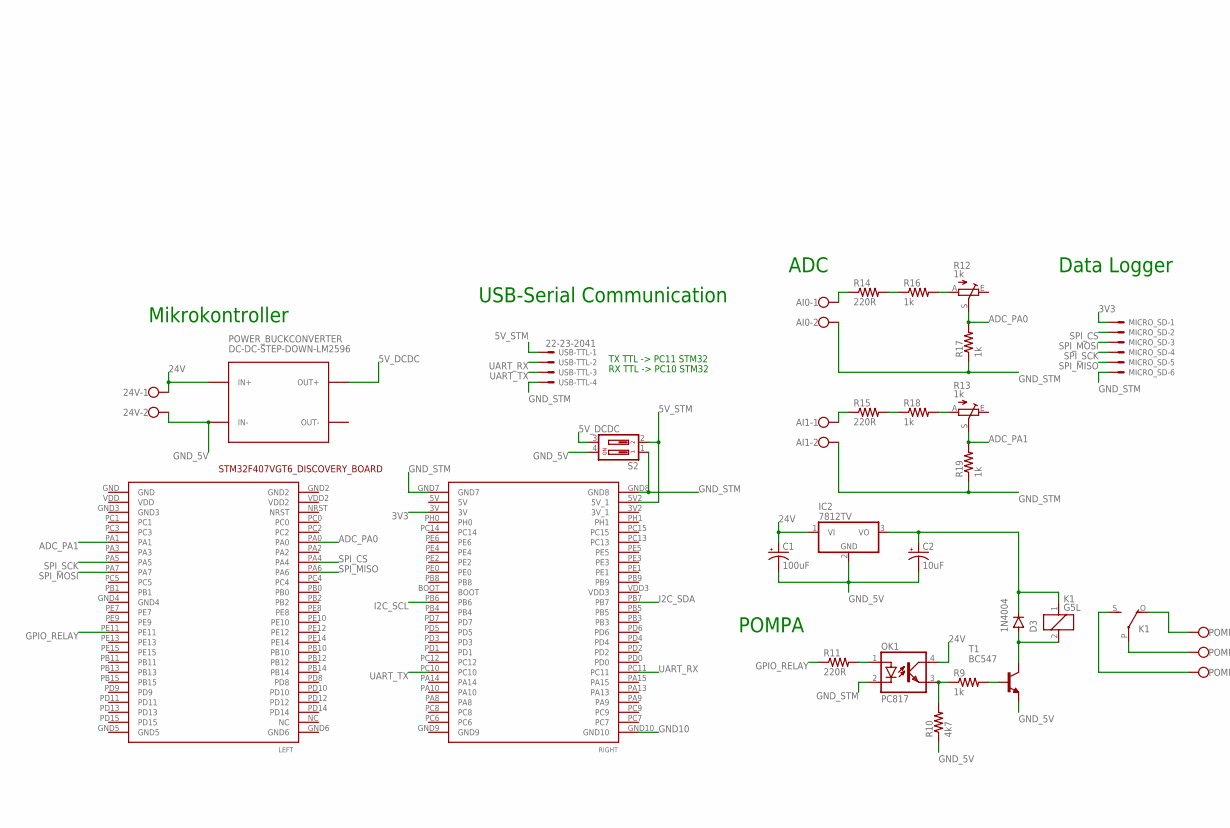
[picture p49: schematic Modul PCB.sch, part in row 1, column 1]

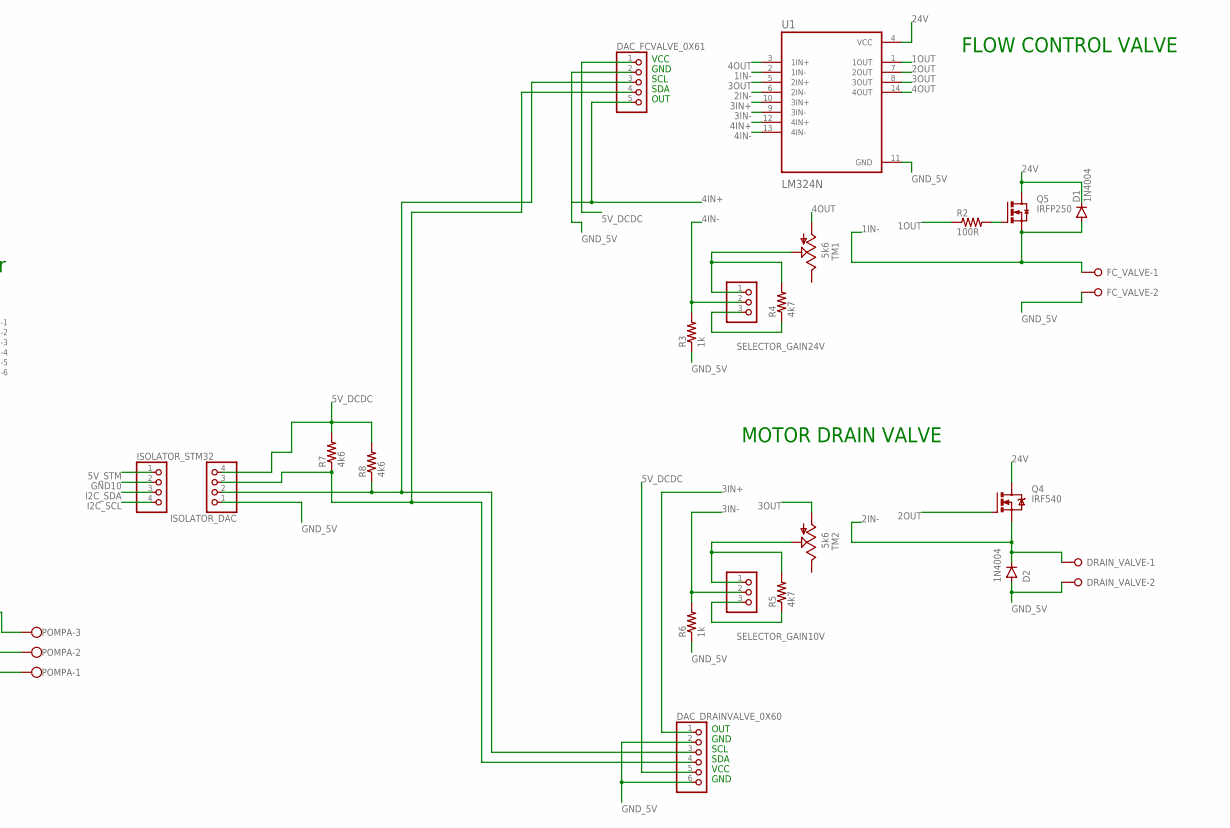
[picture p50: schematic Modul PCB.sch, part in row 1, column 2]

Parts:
24V: W237-102
AI0, AI1: W237-102
C1: 100uF; E2,5-6
C2: 10uF; E2,5-6
D1, D2, D3: 1N4004; DO41-10
DAC_DRAINVALVE_0X60: PINHD-1X6; 1X06
DAC_FCVALVE_0X61: PINHD-1X5; 1X05
DRAIN_VALVE: W237-02P; W237-132
FC_VALVE: W237-02P; W237-132
IC2: 7812TV; TO220V
ISOLATOR_DAC: PINHD-1X4; 1X04
ISOLATOR_STM32: PINHD-1X4; 1X04
K1: G5L; G5LE
MICRO_SD: 22-23-2061
OK1: PC817; DIL04
POMPA: W237-103
POWER_BUCKCONVERTER: DC-DC-STEP-DOWN-LM2596
Q4: IRF540; TO220BV
Q5: IRFP250; TO-247AD-V
R2: 100R; 0207/10
R3, R6, R9, R16, R17, R18, R19: 1k; 0207/10
R4, R5, R10: 4k7; 0207/10
R7, R8: 4k6; 0207/10
R11, R14, R15: 220R; 0207/10
R12, R13: 1k; RJ9W
S2: DS02; DS-02
SELECTOR_GAIN10V, SELECTOR_GAIN24V: PINHD-1X3; 1X03
STM32F407VGT6_DISCOVERY_BOARD: STM32F4-DISCOVERY; STM32F407VG
T1: BC547; TO92
TM1, TM2: 5k6; 6MM
U1: LM324N; DIP794W45P254L1969H508Q14
USB-TTL: 22-23-2041

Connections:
1IN-: D1.A, FC_VALVE.1, Q5.S, U1.2 (1IN-)
1OUT: R2.1, U1.1 (1OUT)
2IN-: D2.C, DRAIN_VALVE.1, Q4.S, U1.6 (2IN-)
2OUT: Q4.G, U1.7 (2OUT)
3IN+: DAC_DRAINVALVE_0X60.1, U1.10 (3IN+)
3IN-: R6.2, SELECTOR_GAIN10V.2, U1.9 (3IN-)
3OUT: TM2.A, U1.5 (2IN+), U1.8 (3OUT)
3V3: MICRO_SD.1, STM32F407VGT6_DISCOVERY_BOARD.3V
4IN+: DAC_FCVALVE_0X61.5, U1.12 (4IN+)
4IN-: R3.2, SELECTOR_GAIN24V.2, U1.13 (4IN-)
4OUT: TM1.A, U1.3 (1IN+), U1.14 (4OUT)
5V_DCDC: DAC_DRAINVALVE_0X60.5, DAC_FCVALVE_0X61.1, ISOLATOR_DAC.4, POWER_BUCKCONVERTER.OUT+, R7.2, R8.2, S2.3
5V_STM: ISOLATOR_STM32.1, S2.2, STM32F407VGT6_DISCOVERY_BOARD.5V2 (5V_1), USB-TTL.1
24V: 24V.1, C1.+, D1.C, IC2.1 (VI), OK1.4 (COL), POWER_BUCKCONVERTER.IN+, Q4.D, Q5.D, U1.4 (VCC)
ADC_PA0: R12.S, R17.2, STM32F407VGT6_DISCOVERY_BOARD.PA0
ADC_PA1: R13.S, R19.2, STM32F407VGT6_DISCOVERY_BOARD.PA1
GND10: ISOLATOR_STM32.2, STM32F407VGT6_DISCOVERY_BOARD.GND10
GND_5V: 24V.2, C1.-, C2.-, D2.A, DAC_DRAINVALVE_0X60.2, DAC_DRAINVALVE_0X60.6, DAC_FCVALVE_0X61.2, DRAIN_VALVE.2, FC_VALVE.2, IC2.2 (GND), ISOLATOR_DAC.1, POWER_BUCKCONVERTER.IN-, R3.1, R6.1, R10.1, S2.4, T1.1 (E), U1.11 (GND)
GND_STM: AI0.2, AI1.2, MICRO_SD.6, OK1.2 (C), R17.1, R19.1, S2.1, STM32F407VGT6_DISCOVERY_BOARD.GND7, STM32F407VGT6_DISCOVERY_BOARD.GND8, USB-TTL.4
GPIO_RELAY: R11.1, STM32F407VGT6_DISCOVERY_BOARD.PE11
I2C_SCL: ISOLATOR_STM32.4, STM32F407VGT6_DISCOVERY_BOARD.PB6
I2C_SDA: ISOLATOR_STM32.3, STM32F407VGT6_DISCOVERY_BOARD.PB7
unnamed: Q5.G, R2.2
unnamed: R4.1, SELECTOR_GAIN24V.3
unnamed: R4.2, SELECTOR_GAIN24V.1, TM1.S
unnamed: R5.2, SELECTOR_GAIN10V.1, TM2.S
unnamed: R5.1, SELECTOR_GAIN10V.3
unnamed: R9.2, T1.2 (B)
unnamed: DAC_DRAINVALVE_0X60.4, DAC_FCVALVE_0X61.4, ISOLATOR_DAC.3, R7.1
unnamed: DAC_DRAINVALVE_0X60.3, DAC_FCVALVE_0X61.3, ISOLATOR_DAC.2, R8.1
unnamed: D3.A, K1.2, T1.3 (C)
unnamed: OK1.3 (EMIT), R9.1, R10.2
unnamed: K1.P, POMPA.2
unnamed: K1.S, POMPA.1
unnamed: K1.O, POMPA.3
unnamed: OK1.1 (A), R11.2
unnamed: AI0.1, R14.1
unnamed: R14.2, R16.1
unnamed: R12.A, R16.2
unnamed: AI1.1, R15.1
unnamed: R15.2, R18.1
unnamed: R13.A, R18.2
unnamed: C2.+, D3.C, IC2.3 (VO), K1.1
SPI_CS: MICRO_SD.2, STM32F407VGT6_DISCOVERY_BOARD.PA4
SPI_MISO: MICRO_SD.5, STM32F407VGT6_DISCOVERY_BOARD.PA6
SPI_MOSI: MICRO_SD.3, STM32F407VGT6_DISCOVERY_BOARD.PA7
SPI_SCK: MICRO_SD.4, STM32F407VGT6_DISCOVERY_BOARD.PA5
UART_RX: STM32F407VGT6_DISCOVERY_BOARD.PC11, USB-TTL.2
UART_TX: STM32F407VGT6_DISCOVERY_BOARD.PC10, USB-TTL.3

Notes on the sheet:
FLOW CONTROL VALVE
MOTOR DRAIN VALVE
POMPA
ADC
TX TTL -> PC11 STM32
RX TTL -> PC10 STM32
USB-Serial Communication
Data Logger
Mikrokontroller
OUT
GND
SCL
SDA
VCC

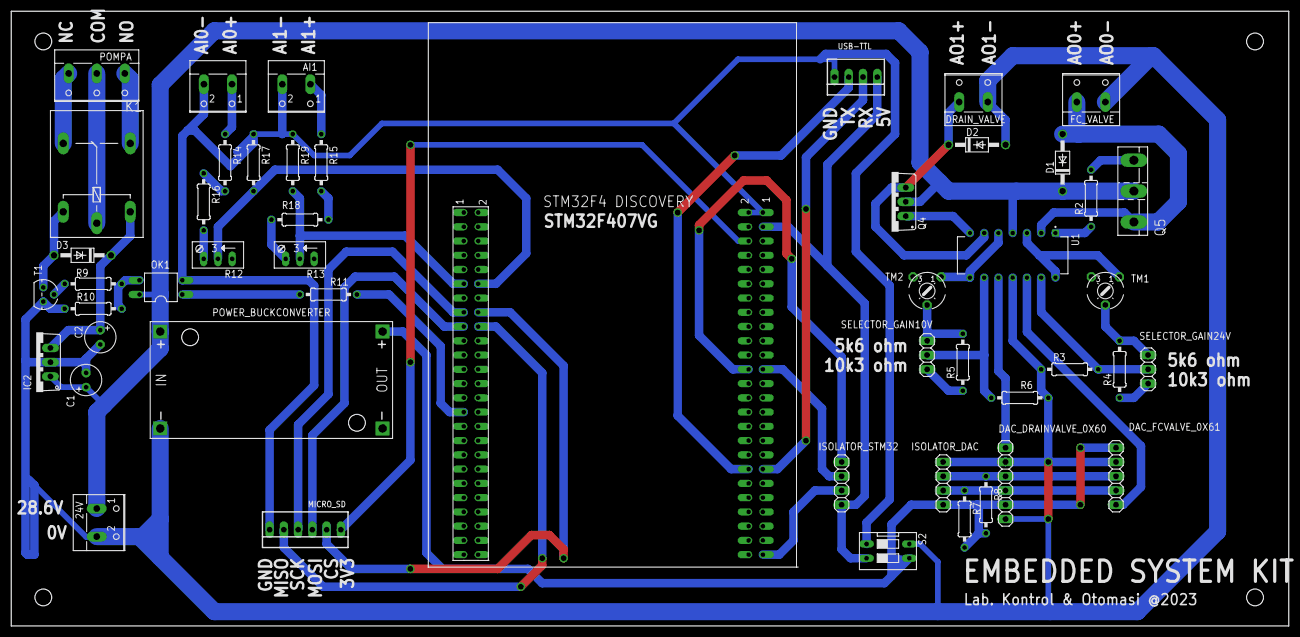
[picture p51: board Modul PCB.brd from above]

Board: 2 copper layers, 227.6 x 109.5 mm, 49 parts (0 on the bottom side), 49 nets.

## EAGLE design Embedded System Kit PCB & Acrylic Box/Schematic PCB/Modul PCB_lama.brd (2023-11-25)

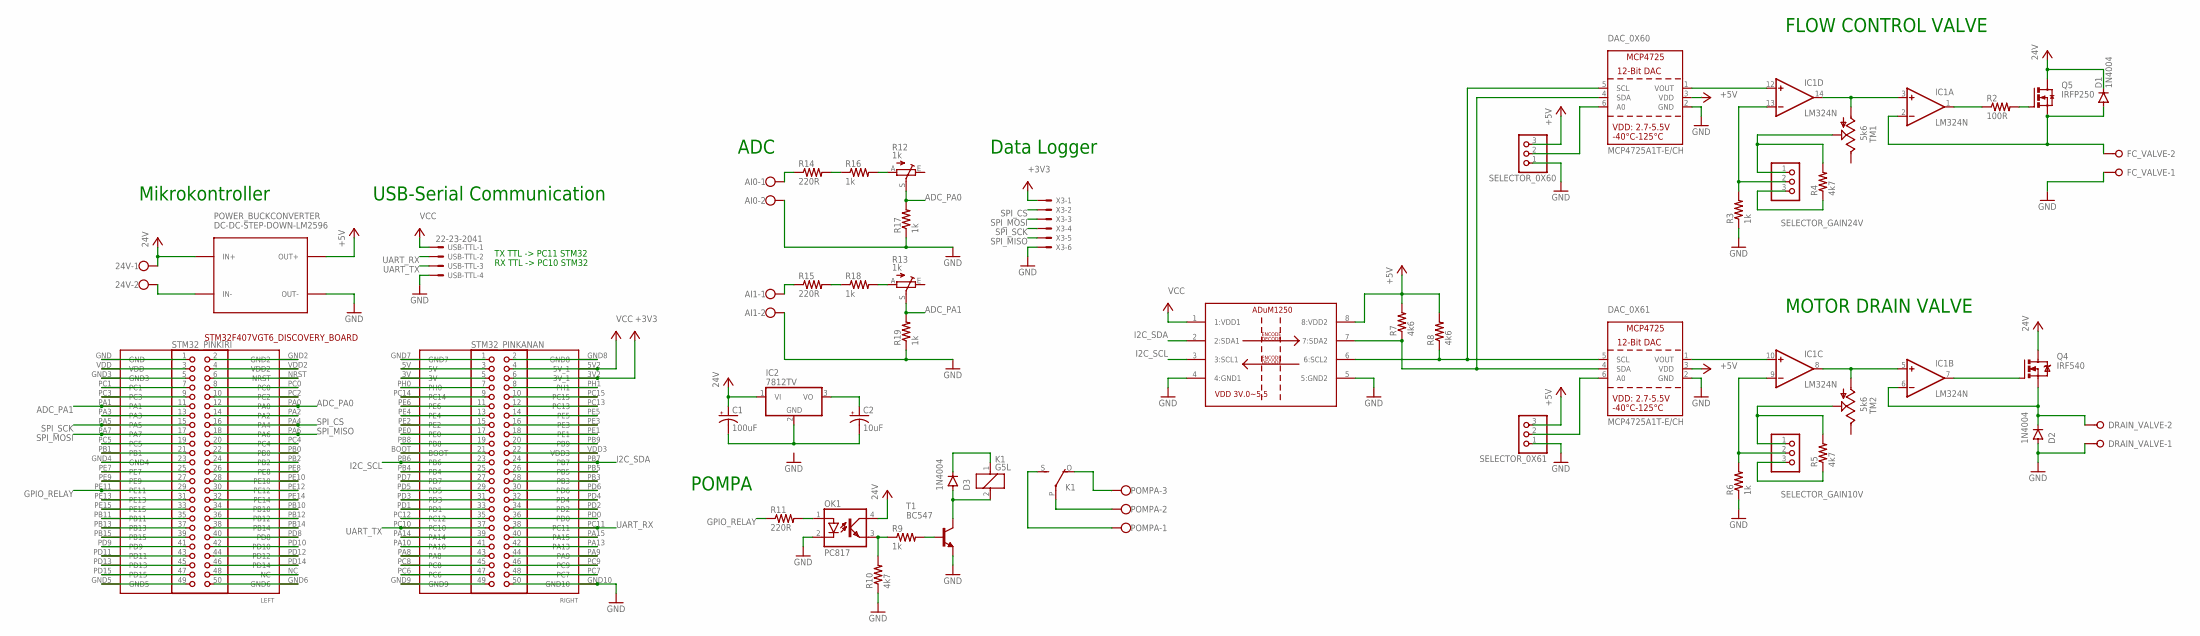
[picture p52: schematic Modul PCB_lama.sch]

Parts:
24V: W237-102
AI0, AI1: W237-102
C1: 100uF; E2,5-6
C2: 10uF; E2,5-6
D1, D2, D3: 1N4004; DO41-10
DAC_0X60, DAC_0X61: MCP4725A1T-E/CH; SOT23-6
DRAIN_VALVE: W237-02P; W237-132
FC_VALVE: W237-02P; W237-132
IC1: LM324N; DIL14
IC2: 7812TV; TO220V
K1: G5L; G5LE
OK1: PC817; DIL04
POMPA: W237-103
POWER_BUCKCONVERTER: DC-DC-STEP-DOWN-LM2596
Q4: IRF540; TO220BV
Q5: IRFP250; TO-247AD-V
R2: 100R; 0207/10
R3, R6, R9, R16, R17, R18, R19: 1k; 0207/10
R4, R5, R10: 4k7; 0207/10
R7, R8: 4k6; 0207/10
R11, R14, R15: 220R; 0207/10
R12, R13: 1k; RJ9W
SELECTOR_0X60, SELECTOR_0X61: PINHD-1X3; 1X03
SELECTOR_GAIN10V, SELECTOR_GAIN24V: PINHD-1X3; 1X03
STM32F407VGT6_DISCOVERY_BOARD: STM32F4-DISCOVERY; STM32F407VG
STM32_PINKANAN, STM32_PINKIRI: PINHD-2X25; 2X25
T1: BC547; TO92
TM1, TM2: 5k6; 6MM
U$1: ADUM1250; SOIC_N
USB-TTL: 22-23-2041
X3: 22-23-2061

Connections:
+3V3: STM32F407VGT6_DISCOVERY_BOARD.3V2 (3V_1), STM32_PINKANAN.6, X3.1
+5V: DAC_0X60.3 (VDD), DAC_0X61.3 (VDD), POWER_BUCKCONVERTER.OUT+, R7.2, R8.2, SELECTOR_0X60.3, SELECTOR_0X61.3, U$1.8 (8:VDD2)
ADC_PA0: R12.S, R17.2, STM32F407VGT6_DISCOVERY_BOARD.PA0, STM32_PINKIRI.12
ADC_PA1: R13.S, R19.2, STM32F407VGT6_DISCOVERY_BOARD.PA1, STM32_PINKIRI.11
GND: AI0.2, AI1.2, D2.A, DAC_0X60.2 (GND), DAC_0X61.2 (GND), DRAIN_VALVE.1, FC_VALVE.1, OK1.2 (C), POWER_BUCKCONVERTER.OUT-, R3.1, R6.1, R10.1, R17.1, R19.1, SELECTOR_0X60.1, SELECTOR_0X61.1, STM32F407VGT6_DISCOVERY_BOARD.GND10, STM32_PINKANAN.50, T1.1 (E), U$1.4 (4:GND1), U$1.5 (5:GND2), USB-TTL.4, X3.6
GPIO_RELAY: R11.1, STM32F407VGT6_DISCOVERY_BOARD.PE11, STM32_PINKIRI.29
I2C_SCL: STM32F407VGT6_DISCOVERY_BOARD.PB6, STM32_PINKANAN.23, U$1.3 (3:SCL1)
I2C_SDA: STM32F407VGT6_DISCOVERY_BOARD.PB7, STM32_PINKANAN.24, U$1.2 (2:SDA1)
unnamed: IC1.1 (OUT), R2.1
unnamed: D2.C, DRAIN_VALVE.2, IC1.6 (-IN), Q4.S
unnamed: IC1.7 (OUT), Q4.G
unnamed: Q5.G, R2.2
unnamed: IC1.3 (+IN), IC1.14 (OUT), TM1.A
unnamed: IC1.5 (+IN), IC1.8 (OUT), TM2.A
unnamed: D1.A, FC_VALVE.2, IC1.2 (-IN), Q5.S
unnamed: IC1.13 (-IN), R3.2, SELECTOR_GAIN24V.2
unnamed: R4.1, SELECTOR_GAIN24V.3
unnamed: R4.2, SELECTOR_GAIN24V.1, TM1.S
unnamed: R5.2, SELECTOR_GAIN10V.1, TM2.S
unnamed: IC1.9 (-IN), R6.2, SELECTOR_GAIN10V.2
unnamed: R5.1, SELECTOR_GAIN10V.3
unnamed: DAC_0X60.1 (VOUT), IC1.12 (+IN)
unnamed: DAC_0X61.1 (VOUT), IC1.10 (+IN)
unnamed: R9.2, T1.2 (B)
unnamed: 24V.2, POWER_BUCKCONVERTER.IN-
unnamed: DAC_0X60.6 (A0), SELECTOR_0X60.2
unnamed: DAC_0X60.4 (SDA), DAC_0X61.4 (SDA), R7.1, U$1.7 (7:SDA2)
unnamed: DAC_0X60.5 (SCL), DAC_0X61.5 (SCL), R8.1, U$1.6 (6:SCL2)
unnamed: D3.A, K1.2, T1.3 (C)
unnamed: DAC_0X61.6 (A0), SELECTOR_0X61.2
unnamed: OK1.3 (EMIT), R9.1, R10.2
unnamed: K1.P, POMPA.2
unnamed: K1.S, POMPA.1
unnamed: K1.O, POMPA.3
unnamed: OK1.1 (A), R11.2
unnamed: AI0.1, R14.1
unnamed: R14.2, R16.1
unnamed: R12.A, R16.2
unnamed: D3.C, K1.1
unnamed: AI1.1, R15.1
unnamed: STM32F407VGT6_DISCOVERY_BOARD.GND, STM32_PINKIRI.1
unnamed: R15.2, R18.1
unnamed: R13.A, R18.2
unnamed: C2.+, IC2.3 (VO)
unnamed: C1.-, C2.-, IC2.2 (GND)
unnamed: STM32F407VGT6_DISCOVERY_BOARD.VDD, STM32_PINKIRI.3
unnamed: STM32F407VGT6_DISCOVERY_BOARD.GND3, STM32_PINKIRI.5
unnamed: STM32F407VGT6_DISCOVERY_BOARD.PC1, STM32_PINKIRI.7
unnamed: STM32F407VGT6_DISCOVERY_BOARD.PC3, STM32_PINKIRI.9
unnamed: STM32F407VGT6_DISCOVERY_BOARD.PA3, STM32_PINKIRI.13
unnamed: STM32F407VGT6_DISCOVERY_BOARD.PC5, STM32_PINKIRI.19
unnamed: STM32F407VGT6_DISCOVERY_BOARD.PB1, STM32_PINKIRI.21
unnamed: STM32F407VGT6_DISCOVERY_BOARD.GND4, STM32_PINKIRI.23
unnamed: STM32F407VGT6_DISCOVERY_BOARD.PE7, STM32_PINKIRI.25
unnamed: STM32F407VGT6_DISCOVERY_BOARD.PE9, STM32_PINKIRI.27
unnamed: STM32F407VGT6_DISCOVERY_BOARD.PE13, STM32_PINKIRI.31
unnamed: STM32F407VGT6_DISCOVERY_BOARD.PE15, STM32_PINKIRI.33
unnamed: STM32F407VGT6_DISCOVERY_BOARD.PB11, STM32_PINKIRI.35
unnamed: STM32F407VGT6_DISCOVERY_BOARD.PB13, STM32_PINKIRI.37
unnamed: STM32F407VGT6_DISCOVERY_BOARD.PB15, STM32_PINKIRI.39
unnamed: STM32F407VGT6_DISCOVERY_BOARD.PD9, STM32_PINKIRI.41
unnamed: STM32F407VGT6_DISCOVERY_BOARD.PD11, STM32_PINKIRI.43
unnamed: STM32F407VGT6_DISCOVERY_BOARD.PD13, STM32_PINKIRI.45
unnamed: STM32F407VGT6_DISCOVERY_BOARD.PD15, STM32_PINKIRI.47
unnamed: STM32F407VGT6_DISCOVERY_BOARD.GND5, STM32_PINKIRI.49
unnamed: STM32F407VGT6_DISCOVERY_BOARD.GND6, STM32_PINKIRI.50
unnamed: STM32F407VGT6_DISCOVERY_BOARD.NC, STM32_PINKIRI.48
unnamed: STM32F407VGT6_DISCOVERY_BOARD.PD14, STM32_PINKIRI.46
unnamed: STM32F407VGT6_DISCOVERY_BOARD.PD12, STM32_PINKIRI.44
unnamed: STM32F407VGT6_DISCOVERY_BOARD.PD10, STM32_PINKIRI.42
unnamed: STM32F407VGT6_DISCOVERY_BOARD.PD8, STM32_PINKIRI.40
unnamed: STM32F407VGT6_DISCOVERY_BOARD.PB14, STM32_PINKIRI.38
unnamed: STM32F407VGT6_DISCOVERY_BOARD.PB12, STM32_PINKIRI.36
unnamed: STM32F407VGT6_DISCOVERY_BOARD.PB10, STM32_PINKIRI.34
unnamed: STM32F407VGT6_DISCOVERY_BOARD.PE14, STM32_PINKIRI.32
unnamed: STM32F407VGT6_DISCOVERY_BOARD.PE12, STM32_PINKIRI.30
unnamed: STM32F407VGT6_DISCOVERY_BOARD.PE10, STM32_PINKIRI.28
unnamed: STM32F407VGT6_DISCOVERY_BOARD.PE8, STM32_PINKIRI.26
unnamed: STM32F407VGT6_DISCOVERY_BOARD.PB2, STM32_PINKIRI.24
unnamed: STM32F407VGT6_DISCOVERY_BOARD.PB0, STM32_PINKIRI.22
unnamed: STM32F407VGT6_DISCOVERY_BOARD.GND2, STM32_PINKIRI.2
unnamed: STM32F407VGT6_DISCOVERY_BOARD.VDD2, STM32_PINKIRI.4
unnamed: STM32F407VGT6_DISCOVERY_BOARD.NRST, STM32_PINKIRI.6
unnamed: STM32F407VGT6_DISCOVERY_BOARD.PC0, STM32_PINKIRI.8
unnamed: STM32F407VGT6_DISCOVERY_BOARD.PC2, STM32_PINKIRI.10
unnamed: STM32F407VGT6_DISCOVERY_BOARD.PA2, STM32_PINKIRI.14
unnamed: STM32F407VGT6_DISCOVERY_BOARD.PC4, STM32_PINKIRI.20
unnamed: STM32F407VGT6_DISCOVERY_BOARD.GND7, STM32_PINKANAN.1
unnamed: STM32F407VGT6_DISCOVERY_BOARD.5V, STM32_PINKANAN.3
unnamed: STM32F407VGT6_DISCOVERY_BOARD.3V, STM32_PINKANAN.5
unnamed: STM32F407VGT6_DISCOVERY_BOARD.PH0, STM32_PINKANAN.7
unnamed: STM32F407VGT6_DISCOVERY_BOARD.PC14, STM32_PINKANAN.9
unnamed: STM32F407VGT6_DISCOVERY_BOARD.PE6, STM32_PINKANAN.11
unnamed: STM32F407VGT6_DISCOVERY_BOARD.PE4, STM32_PINKANAN.13
unnamed: STM32F407VGT6_DISCOVERY_BOARD.PE2, STM32_PINKANAN.15
unnamed: STM32F407VGT6_DISCOVERY_BOARD.PE0, STM32_PINKANAN.17
unnamed: STM32F407VGT6_DISCOVERY_BOARD.PB8, STM32_PINKANAN.19
unnamed: STM32F407VGT6_DISCOVERY_BOARD.BOOT, STM32_PINKANAN.21
unnamed: STM32F407VGT6_DISCOVERY_BOARD.PB4, STM32_PINKANAN.25
unnamed: STM32F407VGT6_DISCOVERY_BOARD.PD7, STM32_PINKANAN.27
unnamed: STM32F407VGT6_DISCOVERY_BOARD.PD5, STM32_PINKANAN.29
unnamed: STM32F407VGT6_DISCOVERY_BOARD.PD3, STM32_PINKANAN.31
unnamed: STM32F407VGT6_DISCOVERY_BOARD.PD1, STM32_PINKANAN.33
unnamed: STM32F407VGT6_DISCOVERY_BOARD.PC12, STM32_PINKANAN.35
unnamed: STM32F407VGT6_DISCOVERY_BOARD.PA14, STM32_PINKANAN.39
unnamed: STM32F407VGT6_DISCOVERY_BOARD.PA10, STM32_PINKANAN.41
unnamed: STM32F407VGT6_DISCOVERY_BOARD.PA8, STM32_PINKANAN.43
unnamed: STM32F407VGT6_DISCOVERY_BOARD.PC8, STM32_PINKANAN.45
unnamed: STM32F407VGT6_DISCOVERY_BOARD.PC6, STM32_PINKANAN.47
unnamed: STM32F407VGT6_DISCOVERY_BOARD.GND9, STM32_PINKANAN.49
unnamed: STM32F407VGT6_DISCOVERY_BOARD.PC7, STM32_PINKANAN.48
unnamed: STM32F407VGT6_DISCOVERY_BOARD.PC9, STM32_PINKANAN.46
unnamed: STM32F407VGT6_DISCOVERY_BOARD.PA9, STM32_PINKANAN.44
unnamed: STM32F407VGT6_DISCOVERY_BOARD.PA13, STM32_PINKANAN.42
unnamed: STM32F407VGT6_DISCOVERY_BOARD.PA15, STM32_PINKANAN.40
unnamed: STM32F407VGT6_DISCOVERY_BOARD.PD0, STM32_PINKANAN.36
unnamed: STM32F407VGT6_DISCOVERY_BOARD.PD2, STM32_PINKANAN.34
unnamed: STM32F407VGT6_DISCOVERY_BOARD.PD4, STM32_PINKANAN.32
unnamed: STM32F407VGT6_DISCOVERY_BOARD.PD6, STM32_PINKANAN.30
unnamed: STM32F407VGT6_DISCOVERY_BOARD.PB3, STM32_PINKANAN.28
unnamed: STM32F407VGT6_DISCOVERY_BOARD.PB5, STM32_PINKANAN.26
unnamed: STM32F407VGT6_DISCOVERY_BOARD.VDD3, STM32_PINKANAN.22
unnamed: STM32F407VGT6_DISCOVERY_BOARD.PB9, STM32_PINKANAN.20
unnamed: STM32F407VGT6_DISCOVERY_BOARD.GND8, STM32_PINKANAN.2
unnamed: STM32F407VGT6_DISCOVERY_BOARD.PH1, STM32_PINKANAN.8
unnamed: STM32F407VGT6_DISCOVERY_BOARD.PC15, STM32_PINKANAN.10
unnamed: STM32F407VGT6_DISCOVERY_BOARD.PC13, STM32_PINKANAN.12
unnamed: STM32F407VGT6_DISCOVERY_BOARD.PE5, STM32_PINKANAN.14
unnamed: STM32F407VGT6_DISCOVERY_BOARD.PE3, STM32_PINKANAN.16
unnamed: STM32F407VGT6_DISCOVERY_BOARD.PE1, STM32_PINKANAN.18
SPI_CS: STM32F407VGT6_DISCOVERY_BOARD.PA4, STM32_PINKIRI.16, X3.2
SPI_MISO: STM32F407VGT6_DISCOVERY_BOARD.PA6, STM32_PINKIRI.18, X3.5
SPI_MOSI: STM32F407VGT6_DISCOVERY_BOARD.PA7, STM32_PINKIRI.17, X3.3
SPI_SCK: STM32F407VGT6_DISCOVERY_BOARD.PA5, STM32_PINKIRI.15, X3.4
UART_RX: STM32F407VGT6_DISCOVERY_BOARD.PC11, STM32_PINKANAN.38, USB-TTL.2
UART_TX: STM32F407VGT6_DISCOVERY_BOARD.PC10, STM32_PINKANAN.37, USB-TTL.3
V+: IC1.4 (V+)
V-: IC1.11 (V-)
VCC: 24V.1, C1.+, D1.C, IC2.1 (VI), OK1.4 (COL), POWER_BUCKCONVERTER.IN+, Q4.D, Q5.D, STM32F407VGT6_DISCOVERY_BOARD.5V2 (5V_1), STM32_PINKANAN.4, U$1.1 (1:VDD1), USB-TTL.1

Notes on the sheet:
FLOW CONTROL VALVE
MOTOR DRAIN VALVE
POMPA
ADC
TX TTL -> PC11 STM32
RX TTL -> PC10 STM32
USB-Serial Communication
Data Logger
Mikrokontroller

Board: 2 copper layers, 51 parts (0 on the bottom side), 137 nets, no tracks yet.

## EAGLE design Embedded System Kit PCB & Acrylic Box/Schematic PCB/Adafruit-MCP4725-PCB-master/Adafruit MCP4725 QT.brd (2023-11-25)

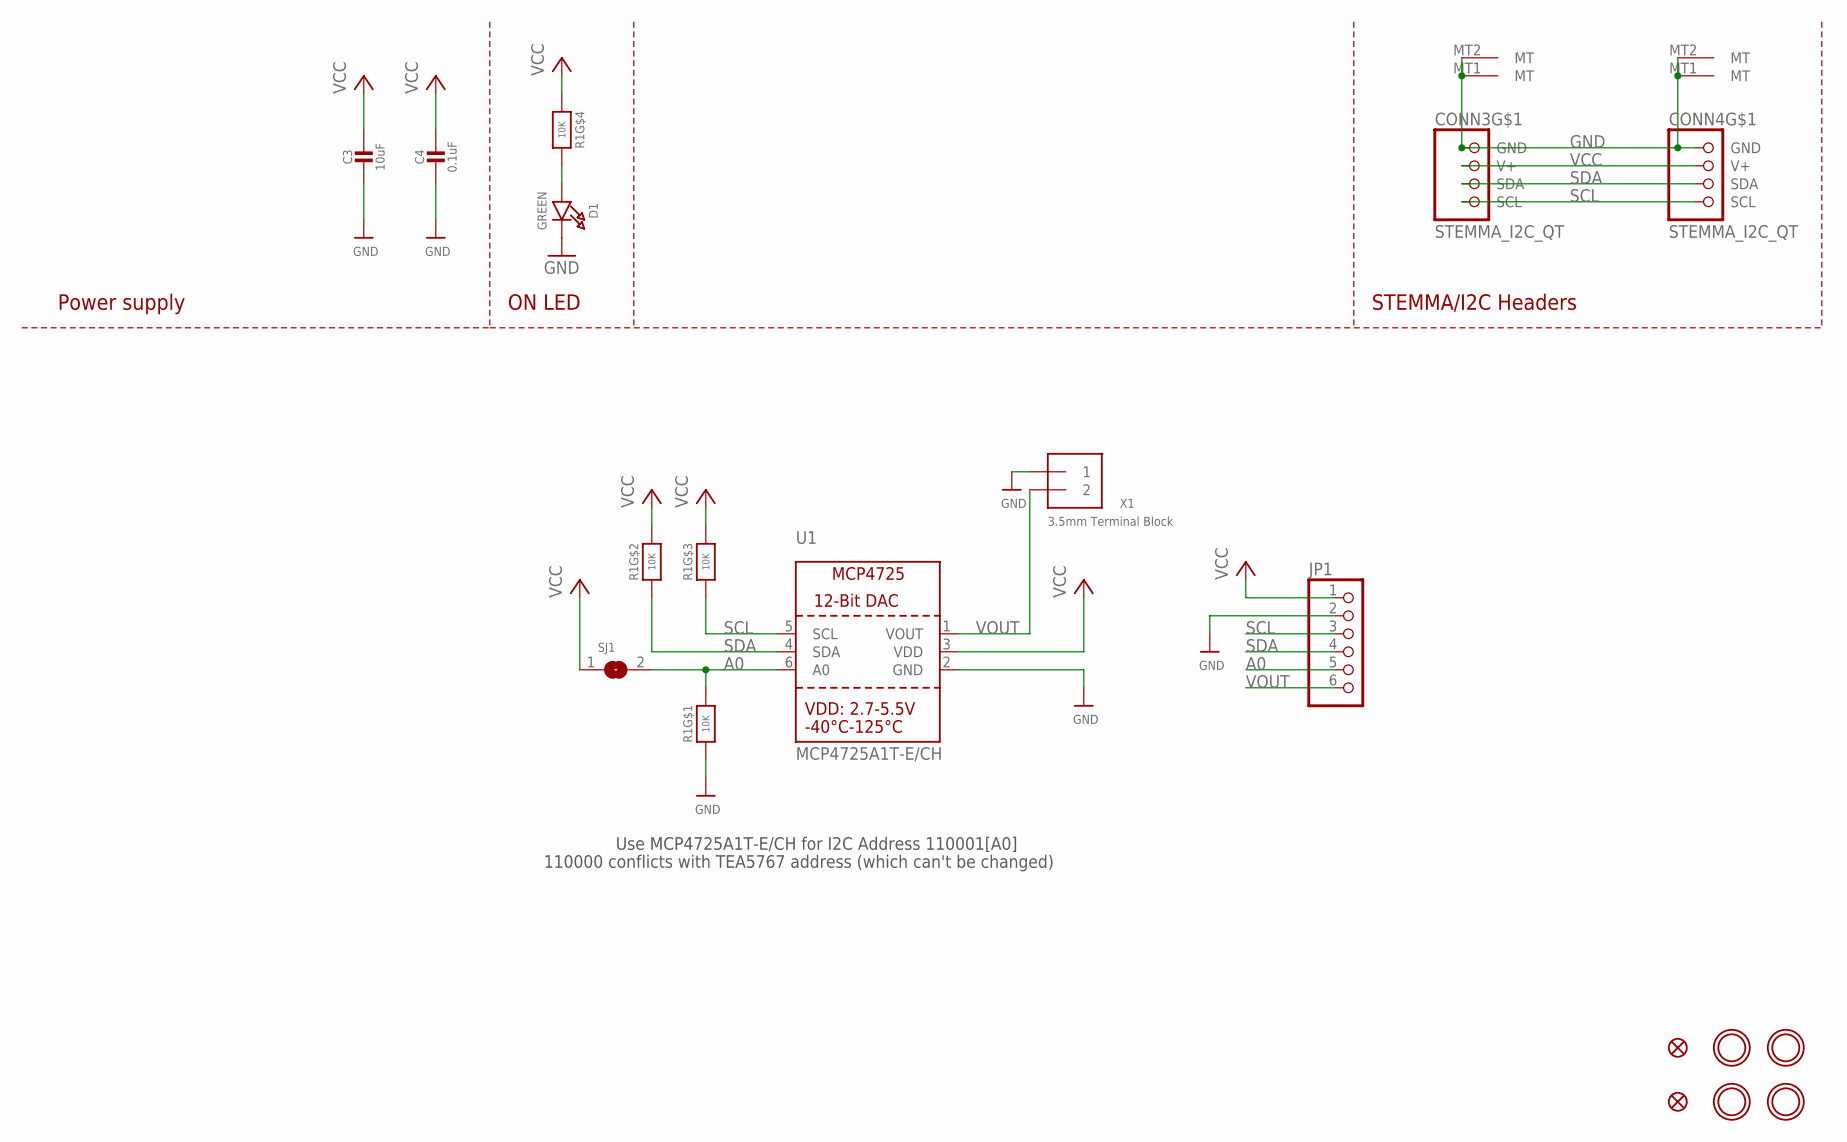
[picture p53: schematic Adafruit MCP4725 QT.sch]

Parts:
C3: 10uF; 0805-NO
C4: 0.1uF; 0603-NO
CONN3, CONN4: STEMMA_I2C_QT; JST_SH4
D1: GREEN; CHIPLED_0603_NOOUTLINE
FID3, FID4: FIDUCIAL_1MM
JP1: HEADER-1X670MIL; 1X06_ROUND_70
R1: 10K; RESPACK_4X0603
SJ1: SOLDERJUMPER; SOLDERJUMPER_ARROW_NOPASTE
U1: MCP4725A1T-E/CH; SOT23-6
U$20, U$21, U$25, U$27: MOUNTINGHOLE2.5; MOUNTINGHOLE_2.5_PLATED
X1: 3.5mm Terminal Block; TERMBLOCK_1X2-3.5MM

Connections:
A0: JP1.5, R1.8 (2), SJ1.2, U1.6 (A0)
GND: C3.2, C4.2, CONN3.1 (GND), CONN3.MT1 (MT), CONN3.MT2 (MT), CONN4.1 (GND), CONN4.MT1 (MT), CONN4.MT2 (MT), D1.C, JP1.2, R1.1, U1.2 (GND), X1.1
unnamed: D1.A, R1.5 (2)
SCL: CONN3.4 (SCL), CONN4.4 (SCL), JP1.3, R1.3 (1), U1.5 (SCL)
SDA: CONN3.3 (SDA), CONN4.3 (SDA), JP1.4, R1.2 (1), U1.4 (SDA)
VCC: C3.1, C4.1, CONN3.2 (V+), CONN4.2 (V+), JP1.1, R1.4 (1), R1.6 (2), R1.7 (2), SJ1.1, U1.3 (VDD)
VOUT: JP1.6, U1.1 (VOUT), X1.2

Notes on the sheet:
STEMMA/I2C Headers
ON LED
Power supply
Use MCP4725A1T-E/CH for I2C Address 110001[A0]
110000 conflicts with TEA5767 address (which can't be changed)

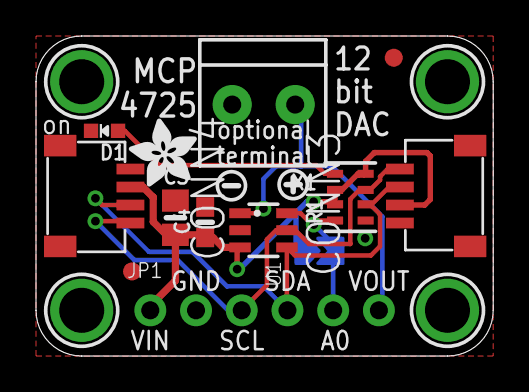
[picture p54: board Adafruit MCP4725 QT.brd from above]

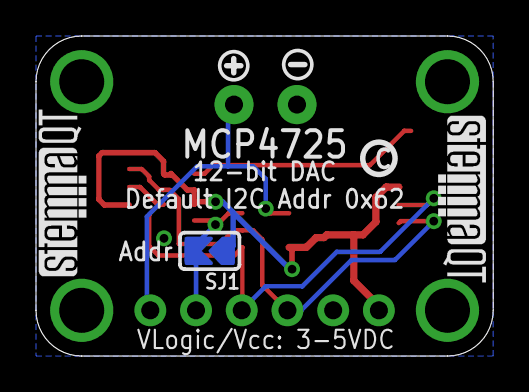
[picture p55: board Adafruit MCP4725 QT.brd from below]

Board: 2 copper layers, 25.4 x 17.8 mm, 24 parts (6 on the bottom side), 7 nets.

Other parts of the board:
U$2, U$7: SYMBOL_PLUS
U$4, U$5: SYMBOL_MINUS
U$8: PCBFEAT-REV-040
U$29: ADAFRUIT_3.5MM
U$31, U$32: STEMMAQT

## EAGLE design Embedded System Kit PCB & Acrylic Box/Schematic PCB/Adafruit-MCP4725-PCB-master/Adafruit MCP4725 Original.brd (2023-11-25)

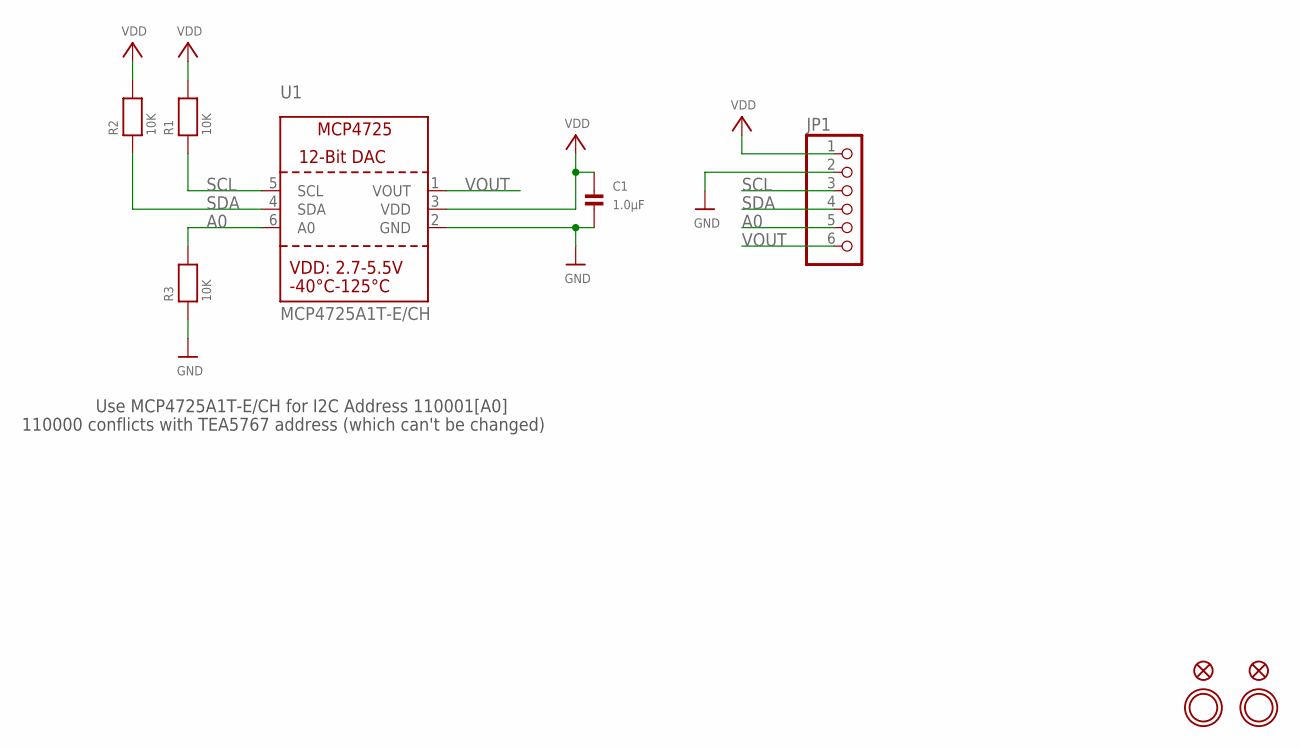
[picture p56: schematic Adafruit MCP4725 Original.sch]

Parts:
C1: 1.0µF; 0805
FID1, FID2: FIDUCIAL""; FIDUCIAL_1MM
JP1: HEADER-1X670MIL; 1X06_ROUND_70
R1, R2, R3: 10K; 0805
U1: MCP4725A1T-E/CH; SOT23-6
U$7, U$8: MOUNTINGHOLE2.5; MOUNTINGHOLE_2.5_PLATED

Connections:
A0: JP1.5, R3.2, U1.6 (A0)
GND: C1.2, JP1.2, R3.1, U1.2 (GND)
SCL: JP1.3, R1.1, U1.5 (SCL)
SDA: JP1.4, R2.1, U1.4 (SDA)
VDD: C1.1, JP1.1, R1.2, R2.2, U1.3 (VDD)
VOUT: JP1.6, U1.1 (VOUT)

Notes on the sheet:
Use MCP4725A1T-E/CH for I2C Address 110001[A0]
110000 conflicts with TEA5767 address (which can't be changed)

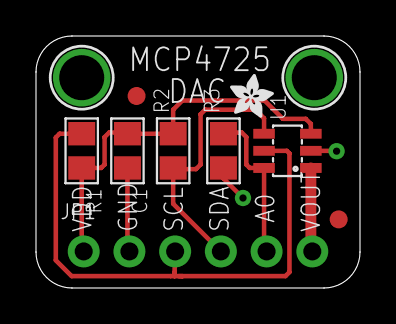
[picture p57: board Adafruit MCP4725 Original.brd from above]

Board: 2 copper layers, 18.0 x 14.0 mm, 11 parts (0 on the bottom side), 6 nets.

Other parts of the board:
U$11: ADAFRUIT_2.5MM

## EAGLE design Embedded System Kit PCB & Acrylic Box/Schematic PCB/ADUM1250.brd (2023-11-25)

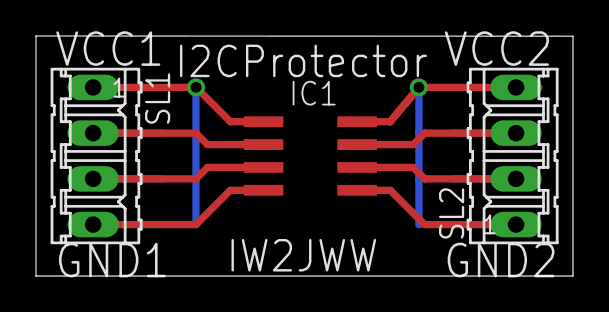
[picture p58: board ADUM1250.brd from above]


Board: 2 copper layers, 29.8 x 13.3 mm, 9 parts (6 on the bottom side), 8 nets.

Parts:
C1, C2: 100nF; C0805
IC1: ADUM1250; SO8
R1, R2, R3, R4: 3k3; M0805
SL1, SL2: 04P

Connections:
GND1: C1.1, IC1.4, SL1.4
GND2: C2.1, IC1.5, SL2.1
unnamed: IC1.2, R1.2, SL1.2
unnamed: IC1.3, R2.1, SL1.3
unnamed: IC1.6, R3.1, SL2.2
unnamed: IC1.7, R4.1, SL2.3
VDD1: C1.2, IC1.1, R1.1, R2.2, SL1.1
VDD2: C2.2, IC1.8, R3.2, R4.2, SL2.4

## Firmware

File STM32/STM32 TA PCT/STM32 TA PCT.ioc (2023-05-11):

#MicroXplorer Configuration settings - do not modify
File.Version=6
GPIO.groupedBy=Group By Peripherals
KeepUserPlacement=false
Mcu.Family=STM32F4
Mcu.IP0=I2C1
Mcu.IP1=NVIC
Mcu.IP2=RCC
Mcu.IP3=SYS
Mcu.IP4=USART1
Mcu.IPNb=5
Mcu.Name=STM32F407V(E-G)Tx
Mcu.Package=LQFP100
Mcu.Pin0=PD12
Mcu.Pin1=PD13
Mcu.Pin2=PA9
Mcu.Pin3=PA10
Mcu.Pin4=PA13
Mcu.Pin5=PA14
Mcu.Pin6=PB6
Mcu.Pin7=PB7
Mcu.Pin8=VP_SYS_VS_Systick
Mcu.PinsNb=9
Mcu.ThirdPartyNb=0
Mcu.UserConstants=
Mcu.UserName=STM32F407VGTx
MxCube.Version=6.4.0
MxDb.Version=DB.6.0.40
NVIC.BusFault_IRQn=true\:0\:0\:false\:false\:true\:false\:false
NVIC.DebugMonitor_IRQn=true\:0\:0\:false\:false\:true\:false\:false
NVIC.ForceEnableDMAVector=true
NVIC.HardFault_IRQn=true\:0\:0\:false\:false\:true\:false\:false
NVIC.MemoryManagement_IRQn=true\:0\:0\:false\:false\:true\:false\:false
NVIC.NonMaskableInt_IRQn=true\:0\:0\:false\:false\:true\:false\:false
NVIC.PendSV_IRQn=true\:0\:0\:false\:false\:true\:false\:false
NVIC.PriorityGroup=NVIC_PRIORITYGROUP_4
NVIC.SVCall_IRQn=true\:0\:0\:false\:false\:true\:false\:false
NVIC.SysTick_IRQn=true\:15\:0\:false\:false\:true\:false\:true
NVIC.UsageFault_IRQn=true\:0\:0\:false\:false\:true\:false\:false
PA10.Mode=Asynchronous
PA10.Signal=USART1_RX
PA13.Mode=Serial_Wire
PA13.Signal=SYS_JTMS-SWDIO
PA14.Mode=Serial_Wire
PA14.Signal=SYS_JTCK-SWCLK
PA9.Mode=Asynchronous
PA9.Signal=USART1_TX
PB6.Mode=I2C
PB6.Signal=I2C1_SCL
PB7.Mode=I2C
PB7.Signal=I2C1_SDA
PD12.Locked=true
PD12.Signal=GPIO_Input
PD13.Locked=true
PD13.Signal=GPIO_Output
PinOutPanel.RotationAngle=0
ProjectManager.AskForMigrate=true
ProjectManager.BackupPrevious=false
ProjectManager.CompilerOptimize=6
ProjectManager.ComputerToolchain=false
ProjectManager.CoupleFile=false
ProjectManager.CustomerFirmwarePackage=
ProjectManager.DefaultFWLocation=true
ProjectManager.DeletePrevious=true
ProjectManager.DeviceId=STM32F407VGTx
ProjectManager.FirmwarePackage=STM32Cube FW_F4 V1.26.2
ProjectManager.FreePins=false
ProjectManager.HalAssertFull=false
ProjectManager.HeapSize=0x200
ProjectManager.KeepUserCode=true
ProjectManager.LastFirmware=true
ProjectManager.LibraryCopy=1
ProjectManager.MainLocation=Core/Src
ProjectManager.NoMain=false
ProjectManager.PreviousToolchain=
ProjectManager.ProjectBuild=false
ProjectManager.ProjectFileName=STM32 TA PCT.ioc
ProjectManager.ProjectName=STM32 TA PCT
ProjectManager.RegisterCallBack=
ProjectManager.StackSize=0x400
ProjectManager.TargetToolchain=STM32CubeIDE
ProjectManager.ToolChainLocation=
ProjectManager.UnderRoot=true
ProjectManager.functionlistsort=1-SystemClock_Config-RCC-false-HAL-false,2-MX_GPIO_Init-GPIO-false-HAL-true,3-MX_TIM1_Init-TIM1-false-HAL-true,4-MX_I2C1_Init-I2C1-false-HAL-true,5-MX_USART1_UART_Init-USART1-false-HAL-true
RCC.48MHZClocksFreq_Value=48000000
RCC.AHBFreq_Value=16000000
RCC.APB1CLKDivider=RCC_HCLK_DIV2
RCC.APB1Freq_Value=8000000
RCC.APB1TimFreq_Value=16000000
RCC.APB2Freq_Value=16000000
RCC.APB2TimFreq_Value=16000000
RCC.CortexFreq_Value=16000000
RCC.EthernetFreq_Value=16000000
RCC.FCLKCortexFreq_Value=16000000
RCC.FamilyName=M
RCC.HCLKFreq_Value=16000000
RCC.HSE_VALUE=25000000
RCC.HSI_VALUE=16000000
RCC.I2SClocksFreq_Value=96000000
RCC.IPParameters=48MHZClocksFreq_Value,AHBFreq_Value,APB1CLKDivider,APB1Freq_Value,APB1TimFreq_Value,APB2Freq_Value,APB2TimFreq_Value,CortexFreq_Value,EthernetFreq_Value,FCLKCortexFreq_Value,FamilyName,HCLKFreq_Value,HSE_VALUE,HSI_VALUE,I2SClocksFreq_Value,LSE_VALUE,LSI_VALUE,MCO2PinFreq_Value,PLLCLKFreq_Value,PLLQCLKFreq_Value,RTCFreq_Value,RTCHSEDivFreq_Value,SYSCLKFreq_VALUE,VCOI2SOutputFreq_Value,VCOInputFreq_Value,VCOOutputFreq_Value,VcooutputI2S
RCC.LSE_VALUE=32768
RCC.LSI_VALUE=32000
RCC.MCO2PinFreq_Value=16000000
RCC.PLLCLKFreq_Value=96000000
RCC.PLLQCLKFreq_Value=48000000
RCC.RTCFreq_Value=32000
RCC.RTCHSEDivFreq_Value=12500000
RCC.SYSCLKFreq_VALUE=16000000
RCC.VCOI2SOutputFreq_Value=192000000
RCC.VCOInputFreq_Value=1000000
RCC.VCOOutputFreq_Value=192000000
RCC.VcooutputI2S=96000000
USART1.IPParameters=VirtualMode
USART1.VirtualMode=VM_ASYNC
VP_SYS_VS_Systick.Mode=SysTick
VP_SYS_VS_Systick.Signal=SYS_VS_Systick
board=custom
isbadioc=false

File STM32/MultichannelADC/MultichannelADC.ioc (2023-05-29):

#MicroXplorer Configuration settings - do not modify
ADC1.Channel-0\#ChannelRegularConversion=ADC_CHANNEL_0
ADC1.Channel-1\#ChannelRegularConversion=ADC_CHANNEL_1
ADC1.Channel-2\#ChannelRegularConversion=ADC_CHANNEL_2
ADC1.ClockPrescaler=ADC_CLOCK_SYNC_PCLK_DIV4
ADC1.ContinuousConvMode=ENABLE
ADC1.DMAContinuousRequests=ENABLE
ADC1.IPParameters=Rank-0\#ChannelRegularConversion,master,Channel-0\#ChannelRegularConversion,SamplingTime-0\#ChannelRegularConversion,NbrOfConversionFlag,ClockPrescaler,ScanConvMode,ContinuousConvMode,DMAContinuousRequests,Rank-1\#ChannelRegularConversion,Channel-1\#ChannelRegularConversion,SamplingTime-1\#ChannelRegularConversion,Rank-2\#ChannelRegularConversion,Channel-2\#ChannelRegularConversion,SamplingTime-2\#ChannelRegularConversion,NbrOfConversion
ADC1.NbrOfConversion=3
ADC1.NbrOfConversionFlag=1
ADC1.Rank-0\#ChannelRegularConversion=1
ADC1.Rank-1\#ChannelRegularConversion=2
ADC1.Rank-2\#ChannelRegularConversion=3
ADC1.SamplingTime-0\#ChannelRegularConversion=ADC_SAMPLETIME_480CYCLES
ADC1.SamplingTime-1\#ChannelRegularConversion=ADC_SAMPLETIME_480CYCLES
ADC1.SamplingTime-2\#ChannelRegularConversion=ADC_SAMPLETIME_480CYCLES
ADC1.ScanConvMode=ENABLE
ADC1.master=1
Dma.ADC1.0.Direction=DMA_PERIPH_TO_MEMORY
Dma.ADC1.0.FIFOMode=DMA_FIFOMODE_DISABLE
Dma.ADC1.0.Instance=DMA2_Stream0
Dma.ADC1.0.MemDataAlignment=DMA_MDATAALIGN_WORD
Dma.ADC1.0.MemInc=DMA_MINC_ENABLE
Dma.ADC1.0.Mode=DMA_CIRCULAR
Dma.ADC1.0.PeriphDataAlignment=DMA_PDATAALIGN_WORD
Dma.ADC1.0.PeriphInc=DMA_PINC_DISABLE
Dma.ADC1.0.Priority=DMA_PRIORITY_LOW
Dma.ADC1.0.RequestParameters=Instance,Direction,PeriphInc,MemInc,PeriphDataAlignment,MemDataAlignment,Mode,Priority,FIFOMode
Dma.Request0=ADC1
Dma.RequestsNb=1
File.Version=6
GPIO.groupedBy=Group By Peripherals
I2C1.IPParameters=OwnAddress
I2C1.OwnAddress=0
I2C2.DualAddressMode=I2C_DUALADDRESS_DISABLE
I2C2.IPParameters=OwnAddress,DualAddressMode
I2C2.OwnAddress=1
KeepUserPlacement=false
Mcu.Family=STM32F4
Mcu.IP0=ADC1
Mcu.IP1=DMA
Mcu.IP10=UART4
Mcu.IP2=FATFS
Mcu.IP3=I2C1
Mcu.IP4=I2C2
Mcu.IP5=NVIC
Mcu.IP6=RCC
Mcu.IP7=SPI1
Mcu.IP8=SYS
Mcu.IP9=TIM1
Mcu.IPNb=11
Mcu.Name=STM32F407V(E-G)Tx
Mcu.Package=LQFP100
Mcu.Pin0=PH0-OSC_IN
Mcu.Pin1=PH1-OSC_OUT
Mcu.Pin10=PE11
Mcu.Pin11=PB10
Mcu.Pin12=PB11
Mcu.Pin13=PA13
Mcu.Pin14=PA14
Mcu.Pin15=PC10
Mcu.Pin16=PC11
Mcu.Pin17=PB6
Mcu.Pin18=PB7
Mcu.Pin19=VP_FATFS_VS_Generic
Mcu.Pin2=PA0-WKUP
Mcu.Pin20=VP_SYS_VS_Systick
Mcu.Pin21=VP_TIM1_VS_ClockSourceINT
Mcu.Pin3=PA1
Mcu.Pin4=PA2
Mcu.Pin5=PA4
Mcu.Pin6=PA5
Mcu.Pin7=PA6
Mcu.Pin8=PA7
Mcu.Pin9=PE9
Mcu.PinsNb=22
Mcu.ThirdPartyNb=0
Mcu.UserConstants=
Mcu.UserName=STM32F407VGTx
MxCube.Version=6.4.0
MxDb.Version=DB.6.0.40
NVIC.BusFault_IRQn=true\:0\:0\:false\:false\:true\:false\:false
NVIC.DMA2_Stream0_IRQn=true\:0\:0\:false\:false\:true\:false\:true
NVIC.DebugMonitor_IRQn=true\:0\:0\:false\:false\:true\:false\:false
NVIC.ForceEnableDMAVector=true
NVIC.HardFault_IRQn=true\:0\:0\:false\:false\:true\:false\:false
NVIC.MemoryManagement_IRQn=true\:0\:0\:false\:false\:true\:false\:false
NVIC.NonMaskableInt_IRQn=true\:0\:0\:false\:false\:true\:false\:false
NVIC.PendSV_IRQn=true\:0\:0\:false\:false\:true\:false\:false
NVIC.PriorityGroup=NVIC_PRIORITYGROUP_4
NVIC.SVCall_IRQn=true\:0\:0\:false\:false\:true\:false\:false
NVIC.SysTick_IRQn=true\:15\:0\:false\:false\:true\:false\:true
NVIC.UsageFault_IRQn=true\:0\:0\:false\:false\:true\:false\:false
PA0-WKUP.Signal=ADCx_IN0
PA1.Signal=ADCx_IN1
PA13.Mode=Serial_Wire
PA13.Signal=SYS_JTMS-SWDIO
PA14.Mode=Serial_Wire
PA14.Signal=SYS_JTCK-SWCLK
PA2.Signal=ADCx_IN2
PA4.GPIOParameters=GPIO_PuPd
PA4.GPIO_PuPd=GPIO_PULLUP
PA4.Locked=true
PA4.Signal=GPIO_Output
PA5.GPIOParameters=GPIO_PuPd
PA5.GPIO_PuPd=GPIO_PULLUP
PA5.Mode=Full_Duplex_Master
PA5.Signal=SPI1_SCK
PA6.GPIOParameters=GPIO_PuPd
PA6.GPIO_PuPd=GPIO_PULLUP
PA6.Mode=Full_Duplex_Master
PA6.Signal=SPI1_MISO
PA7.GPIOParameters=GPIO_PuPd
PA7.GPIO_PuPd=GPIO_PULLUP
PA7.Mode=Full_Duplex_Master
PA7.Signal=SPI1_MOSI
PB10.GPIOParameters=GPIO_Pu
PB10.GPIO_Pu=GPIO_PULLUP
PB10.Mode=I2C
PB10.Signal=I2C2_SCL
PB11.GPIOParameters=GPIO_Pu
PB11.GPIO_Pu=GPIO_PULLUP
PB11.Mode=I2C
PB11.Signal=I2C2_SDA
PB6.GPIOParameters=GPIO_Pu
PB6.GPIO_Pu=GPIO_PULLUP
PB6.Mode=I2C
PB6.Signal=I2C1_SCL
PB7.GPIOParameters=GPIO_Pu
PB7.GPIO_Pu=GPIO_PULLUP
PB7.Mode=I2C
PB7.Signal=I2C1_SDA
PC10.Mode=Asynchronous
PC10.Signal=UART4_TX
PC11.Mode=Asynchronous
PC11.Signal=UART4_RX
PE11.Locked=true
PE11.Signal=GPIO_Output
PE9.Signal=S_TIM1_CH1
PH0-OSC_IN.Mode=HSE-External-Oscillator
PH0-OSC_IN.Signal=RCC_OSC_IN
PH1-OSC_OUT.Mode=HSE-External-Oscillator
PH1-OSC_OUT.Signal=RCC_OSC_OUT
PinOutPanel.RotationAngle=0
ProjectManager.AskForMigrate=true
ProjectManager.BackupPrevious=false
ProjectManager.CompilerOptimize=6
ProjectManager.ComputerToolchain=false
ProjectManager.CoupleFile=true
ProjectManager.CustomerFirmwarePackage=
ProjectManager.DefaultFWLocation=true
ProjectManager.DeletePrevious=true
ProjectManager.DeviceId=STM32F407VGTx
ProjectManager.FirmwarePackage=STM32Cube FW_F4 V1.26.2
ProjectManager.FreePins=false
ProjectManager.HalAssertFull=false
ProjectManager.HeapSize=0x200
ProjectManager.KeepUserCode=true
ProjectManager.LastFirmware=true
ProjectManager.LibraryCopy=1
ProjectManager.MainLocation=Core/Src
ProjectManager.NoMain=false
ProjectManager.PreviousToolchain=
ProjectManager.ProjectBuild=false
ProjectManager.ProjectFileName=MultichannelADC.ioc
ProjectManager.ProjectName=MultichannelADC
ProjectManager.RegisterCallBack=
ProjectManager.StackSize=0x400
ProjectManager.TargetToolchain=STM32CubeIDE
ProjectManager.ToolChainLocation=
ProjectManager.UnderRoot=true
ProjectManager.functionlistsort=1-SystemClock_Config-RCC-false-HAL-false,2-MX_GPIO_Init-GPIO-false-HAL-true,3-MX_DMA_Init-DMA-false-HAL-true,4-MX_ADC1_Init-ADC1-false-HAL-true,5-MX_TIM1_Init-TIM1-false-HAL-true,6-MX_SPI1_Init-SPI1-false-HAL-true,7-MX_FATFS_Init-FATFS-false-HAL-false,8-MX_UART4_Init-UART4-false-HAL-true,9-MX_I2C1_Init-I2C1-false-HAL-true,10-MX_I2C2_Init-I2C2-false-HAL-true
RCC.48MHZClocksFreq_Value=84000000
RCC.AHBFreq_Value=168000000
RCC.APB1CLKDivider=RCC_HCLK_DIV4
RCC.APB1Freq_Value=42000000
RCC.APB1TimFreq_Value=84000000
RCC.APB2CLKDivider=RCC_HCLK_DIV2
RCC.APB2Freq_Value=84000000
RCC.APB2TimFreq_Value=168000000
RCC.CortexFreq_Value=168000000
RCC.EthernetFreq_Value=168000000
RCC.FCLKCortexFreq_Value=168000000
RCC.FamilyName=M
RCC.HCLKFreq_Value=168000000
RCC.HSE_VALUE=8000000
RCC.HSI_VALUE=16000000
RCC.I2SClocksFreq_Value=192000000
RCC.IPParameters=48MHZClocksFreq_Value,AHBFreq_Value,APB1CLKDivider,APB1Freq_Value,APB1TimFreq_Value,APB2CLKDivider,APB2Freq_Value,APB2TimFreq_Value,CortexFreq_Value,EthernetFreq_Value,FCLKCortexFreq_Value,FamilyName,HCLKFreq_Value,HSE_VALUE,HSI_VALUE,I2SClocksFreq_Value,LSE_VALUE,LSI_VALUE,MCO2PinFreq_Value,PLLCLKFreq_Value,PLLM,PLLN,PLLQCLKFreq_Value,PLLSourceVirtual,RTCFreq_Value,RTCHSEDivFreq_Value,SYSCLKFreq_VALUE,SYSCLKSource,VCOI2SOutputFreq_Value,VCOInputFreq_Value,VCOOutputFreq_Value,VcooutputI2S
RCC.LSE_VALUE=32768
RCC.LSI_VALUE=32000
RCC.MCO2PinFreq_Value=168000000
RCC.PLLCLKFreq_Value=168000000
RCC.PLLM=4
RCC.PLLN=168
RCC.PLLQCLKFreq_Value=84000000
RCC.PLLSourceVirtual=RCC_PLLSOURCE_HSE
RCC.RTCFreq_Value=32000
RCC.RTCHSEDivFreq_Value=4000000
RCC.SYSCLKFreq_VALUE=168000000
RCC.SYSCLKSource=RCC_SYSCLKSOURCE_PLLCLK
RCC.VCOI2SOutputFreq_Value=384000000
RCC.VCOInputFreq_Value=2000000
RCC.VCOOutputFreq_Value=336000000
RCC.VcooutputI2S=192000000
SH.ADCx_IN0.0=ADC1_IN0,IN0
SH.ADCx_IN0.ConfNb=1
SH.ADCx_IN1.0=ADC1_IN1,IN1
SH.ADCx_IN1.ConfNb=1
SH.ADCx_IN2.0=ADC1_IN2,IN2
SH.ADCx_IN2.ConfNb=1
SH.S_TIM1_CH1.0=TIM1_CH1,PWM Generation1 CH1
SH.S_TIM1_CH1.ConfNb=1
SPI1.CalculateBaudRate=42.0 MBits/s
SPI1.Direction=SPI_DIRECTION_2LINES
SPI1.IPParameters=VirtualType,Mode,Direction,CalculateBaudRate
SPI1.Mode=SPI_MODE_MASTER
SPI1.VirtualType=VM_MASTER
TIM1.Channel-PWM\ Generation1\ CH1=TIM_CHANNEL_1
TIM1.IPParameters=Channel-PWM Generation1 CH1,Prescaler,Period,RepetitionCounter
TIM1.Period=999
TIM1.Prescaler=335
TIM1.RepetitionCounter=12
UART4.IPParameters=VirtualMode
UART4.VirtualMode=Asynchronous
VP_FATFS_VS_Generic.Mode=User_defined
VP_FATFS_VS_Generic.Signal=FATFS_VS_Generic
VP_SYS_VS_Systick.Mode=SysTick
VP_SYS_VS_Systick.Signal=SYS_VS_Systick
VP_TIM1_VS_ClockSourceINT.Mode=Internal
VP_TIM1_VS_ClockSourceINT.Signal=TIM1_VS_ClockSourceINT
board=custom
isbadioc=false

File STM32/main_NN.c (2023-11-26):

/* USER CODE BEGIN Header */
/**
  ******************************************************************************
  * @file           : main.c
  * @brief          : Main program body
  ******************************************************************************
  * @attention
  *
  * Copyright (c) 2023 STMicroelectronics.
  * All rights reserved.
  *
  * This software is licensed under terms that can be found in the LICENSE file
  * in the root directory of this software component.
  * If no LICENSE file comes with this software, it is provided AS-IS.
  *
  ******************************************************************************
  */
/* USER CODE END Header */
/* Includes ------------------------------------------------------------------*/
#include "main.h"
#include "adc.h"
#include "crc.h"
#include "dma.h"
#include "fatfs.h"
#include "i2c.h"
#include "spi.h"
#include "tim.h"
#include "usart.h"
#include "gpio.h"

/* Private includes ----------------------------------------------------------*/
/* USER CODE BEGIN Includes */
#include "stm32f4xx_hal.h"
#include <stdio.h>
#include <string.h>
#include <stdarg.h> //for va_list var arg functions
#include <stdlib.h>
#include <MCP4725.h>
#include <stdint.h>
#include <math.h>
//#include "user_diskio_spi.h"
//#include "user_diskio.h"
/* USER CODE END Includes */

/* Private typedef -----------------------------------------------------------*/
/* USER CODE BEGIN PTD */

/* USER CODE END PTD */

/* Private define ------------------------------------------------------------*/
/* USER CODE BEGIN PD */
/* USER CODE END PD */

/* Private macro -------------------------------------------------------------*/
/* USER CODE BEGIN PM */

/* USER CODE END PM */

/* Private variables ---------------------------------------------------------*/

/* USER CODE BEGIN PV */
// Initialize matrix for weight input and hidden layer
#define num_neuronHidden 3 // sebagai baris
#define num_neuronInput	 3 // sebagai kolom
// baris: neuronHidden ke-, kolom: neuronInput ke-
float w_input[num_neuronHidden][num_neuronInput];
float v_hidden[num_neuronHidden];
float delta2[num_neuronHidden], hj[num_neuronHidden];
float x_input[num_neuronInput];

float y, Qin; // dalam volt
float SP = 100; // dalam mm
uint8_t dey_deu;

uint32_t my_adc[3];
uint32_t AI0_bit, AI1_bit, AI2_bit;
float AI0_volt, AI1_volt, AI2_volt;
float AO0_volt = 0; // valve flow control Qin
float AO1_volt = 4; // pompa, drain valve
uint16_t AO0_bit, AO1_bit = 0;
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

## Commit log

2023-01-01 change voltage formula, GUI, timestamp
    [dataRafif.csv]
2023-01-01 adding data observation for open loop
    [Analisis Openloop Level Transmitter.xlsx, dataRafif.csv]
2023-01-02 adding level transmitter regression
    [Analisis Openloop Level Transmitter.xlsx]
2023-01-02 changing desired tank level into 20cm, find m & c
2023-01-02 changing desired tank level into 20cm, substitute m & c
2023-01-02 [Worked] Koding closed loop Pak Hady Mas Khoiruz
    [data Closed Loop Khoiruz.csv]
2023-01-02 update closedLoop selasa pagi 5AM
    [dataRafif_FLC.csv]
2023-01-03 adding MQTT feature & its configuration
    [dataRafif_FLC.csv]
2023-01-03 hasil re-run rabu pagi 5AM
    [dataRafif_FLC.csv]
2023-01-11 update condition timeNow-timeLast
    [data Closed Loop Khoiruz.csv]
2023-01-17 Change variable name and adding flow plot (right)
    [data Closed Loop Khoiruz.csv]
2023-01-25 move csv datasets into a new directory
    [Datasets Open Loop Faris Ts 0.05.csv, Datasets Open Loop Faris v0.csv]
2023-01-26 configure inner loop, add SP transfer function from flow into level
2023-02-01 change Gain SP flow, output controller Outer level, from regresi_FT.py (hasil konsul P.Hady)
2023-02-01 add print(flow_sebenarnya) for getting SP inner gain from level loop
2023-05-08 add m_LT, c_LT for flow measurement
2023-05-09 able to approximate flow meter model in lt/min
2023-05-11 Multiple ADC STM can perform open loop for drain valve
2023-05-29 identify Ao valve (man & mov)
    [Datasets Closed Loop Level Bu Tri Kp10, SP10.csv, Datasets Open Loop Faris 10VDC baru Ts0.05.csv, Datasets Open Loop Faris 5VDC Ts0.05.csv, Datasets Open Loop 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]
2023-11-25 add Buying Report.xlsx
    [Rekap Nota Embedded System Kit_Update 19 Nov 2023.xlsx]
2023-11-25 add Rafif level sensor data
    [Analisis Openloop Level Transmitter.xlsx, Rafif analisis data openloop.xlsx]
2023-11-25 add burkert motor valve datasheet
2023-11-25 add PCB Schematic for Implementation
    [ADUM1250.brd, Adafruit MCP4725 Original.brd, Adafruit MCP4725 Original.sch, Adafruit MCP4725 QT.brd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]
2023-11-25 add prototype photo
2023-11-26 add 3D Acrylic Model and 3D Print USB-TTL
    [Alas Bawah.0001.ipt, Alas Bawah.ipt, Assembly Case USB TTL.0002.iam, Assembly Case USB TTL.iam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]
2023-11-26 change folder into Modelling and Testing using ADAM5000L TCP
    [Datasets Closed Loop Level Bu Tri Kp10, SP10.csv, Datasets Open Loop Faris 10VDC baru Ts0.05.csv, Datasets Open Loop Faris 5VDC Ts0.05.csv, Datasets Open Loop 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]
2023-11-26 add ADAM5000L python testing
    [Datasets Closed Loop Level Bu Tri Kp10, SP10.csv, Datasets Open Loop Faris 10VDC baru Ts0.05.csv, Datasets Open Loop Faris 5VDC Ts0.05.csv, Datasets Open Loop 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]
2023-11-26 move into Khoirus & Rafif's folder: PCT100 with ADAM5000L
    [Datasets Closed Loop Level Bu Tri Kp10, SP10.csv, Datasets Open Loop Faris 10VDC baru Ts0.05.csv, Datasets Open Loop Faris 5VDC Ts0.05.csv, Datasets Open Loop 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]
2023-11-26 move into STM32 folder
2023-11-26 move into ADAM4000L folder
    [List Pin IO ADAM.xlsx, Modbus Address Calculator for Unidrive M Rev3.xlsx]
2023-11-26 move respon DAC PWM
    [Kurva respon DAC.xlsx]
2023-11-26 move simulink RC filter to proteus folder
2023-11-27 add TA Dedy Bambang about PID-GA Induction Motor
2024-04-26 add Excel Rekap SKS Matkul
    [Rekap SKS Matkul Muhammad Faris Zuhairi_07111940000164.xlsx]
2024-04-26 add Prototype Documentation
2024-04-26 add PCB Board Cache File

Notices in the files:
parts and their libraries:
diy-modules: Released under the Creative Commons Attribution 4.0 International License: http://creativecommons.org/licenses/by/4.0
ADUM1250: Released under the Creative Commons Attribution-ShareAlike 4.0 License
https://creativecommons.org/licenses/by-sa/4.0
